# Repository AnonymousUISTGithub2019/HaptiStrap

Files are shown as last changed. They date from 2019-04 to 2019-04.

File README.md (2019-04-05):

# What is the HaptiStrap?


How tightly a haptic device, such as a smartwatch, is strapped to the body can change how its vibrotactile effects are perceived.
Although a single researcher may be able to achieve reasonably consistent strap tightness across participants, this may not be easily achievable when multiple, potentially geographically distributed, experimenters are working with different participants.
Likewise, when participants must attach the devices on their own, e.g., during a longitudinal in-the-wild study, they may not use the same tightness each day.

The HaptiStrap is a low-cost, easily fabricated tool, loosely based on the medical Gulick tape measure, that helps to create consistent strap tension, and therefore haptic coupling, for wearable haptic devices used in user studies.
Since it is fabricated using 3d printing, the HaptiStrap can be easily modified to meet the requirements for a variety of body locations and experiment types.
Although HaptiStrap is not yet trialed with users, we present design iterations motivated by problems seen in our own work, as a contribution towards designing a standard method for ensuring that studies do better than vague ``tight but comfortable'' guidelines.

In this repository you will find all necessary files, fabrication, assembly and usage instructions to integrate the HaptiStrap in your project. In addition, since OpenSCAD design files are provided, a short step-by-step example is provided to adapt the HaptiStrap device to a different strap width. 

If you use the HaptiStrap, please do not forget to cite this publication:

INSERT PAPER BILIOGRAPHY ENTRY HERE.

# Table of Content
- [Making your Own HaptiStrap](#making-your-own-haptistrap)
  * [Equipment](#equipment)
  * [Choosing a Tensioner](#choosing-a-tensioner)
  * [3D Printing](#3d-printing)
    + [Get the Files](#get-the-files)
    + [Print the Files](#print-the-files)
  * [Putting it all Together](#putting-it-all-together)
    + [Elastic Tensioner](#elastic-tensioner)
    + [3D Printed Tensioner](#3d-printed-tensioner)
- [Using the HaptiStrap in your Project](#using-the-haptistrap-in-your-project)
  * [Determining how Many Elastics to use](#determining-how-many-elastics-to-use)
  * [Customizing HaptiStrap Dimensions to Match your Project](#customizing-haptistrap-dimensions-to-match-your-project)
  * [Adding the HaptiStrap to your Haptic System](#adding-the-haptistrap-to-your-haptic-system)
  * [Recommended Placement Instructions](#recommended-placement-instructions)
 
# Making your Own Haptistrap 

## Equipment
You will need access to the following equipment to make and assemble your own HaptiStrap:

1. FDM 3D printer
2. PLA filament (approximately 5 g or 2 m)
3. Orthodontic elastics (1/8", 1.8oz)
4. Pointy tweezers (useful for placing the elastics)
5. Highly visible permanent coating material (e.g., white/neon paint/nail polish, liquid paper, etc.)
6. Low-friction tape (e.g., teflon, aluminium, polyethylene tape etc.)

## Choosing a Tensioner

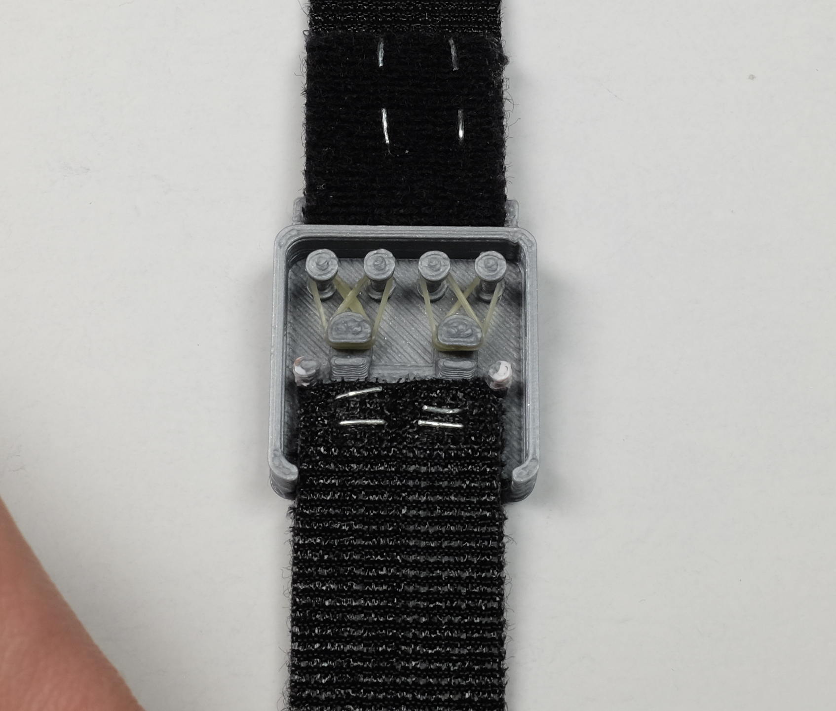
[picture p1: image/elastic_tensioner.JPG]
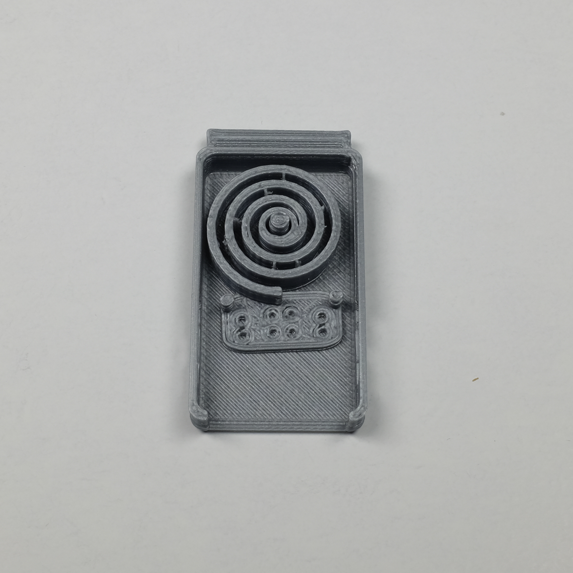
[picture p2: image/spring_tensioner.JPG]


Despite making the 3D printed spring option available, we highly recommend using the elastic tensioner system as it was shown to have more consistent mechanical properties.

## 3D Printing 

### Get the Files

Before printing your own HaptiStrap, you will need to download the pre-rendered STL files or generate them from the provided OpenSCAD design files.

The type of tensioner you want to use dictates the path and file name of the files to download.

| Tensioner Type | File|
|---|---|
|elastic|/stl/elastic/haptistrap_enclosure_elastic.stl|
||/stl/elastic/haptistrap_tensioner_elastic.stl|
||/stl/elastic/haptistrap_elastic_primer.stl|
|3D printed spring|/stl/3dPrintedSpring/haptistrap_enclosure_spring.stl|
||/stl/3dPrintedSpring/haptistrap_tensioner_spring.stl|
||/stl/3dPrintedSpring/haptistrap_spring_primer.stl|

### Print the Files

The HaptiStrap was designed such that it can be printed with the most commonly encountered 3D printer configuration, material (PLA) and slicing settings.

The following slicing parameters were used to obtain the components whose properties were measured and reported in the HaptiStrap paper. While you are free to modify any of them, these modifications could influence the mechanical properties of the produced component. 

| Parameter | Value | Unit |
|---|---|---|
|nozzle size|0.4|mm|
|layer height|0.2|mm|
|line width|0.4|mm|
|wall thickness|0.8|mm|
|top/bottom thickness|0.8|mm|
|infill density|100|%|

Notes:
- Supports should be used to ensure that the calibration windows on each side of the enclosure and lid are properly aligned.
- A brim, skirt or raft can be used to print the enclosure and its lid depending on your bed adhesion.
- For the 3D printed spring tensioner, it is preferable to print on a very smooth surface (e.g., glass, mirror, etc.) as the texture may increase friction between the spring and enclosure. As such, the use of a raft or brim is not recommended.

## Putting it all Together

Separate assembly instructions are provided depending on the type of tensioner used.

### Elastic Tensioner

|Instruction|Picture|
|---|-----|
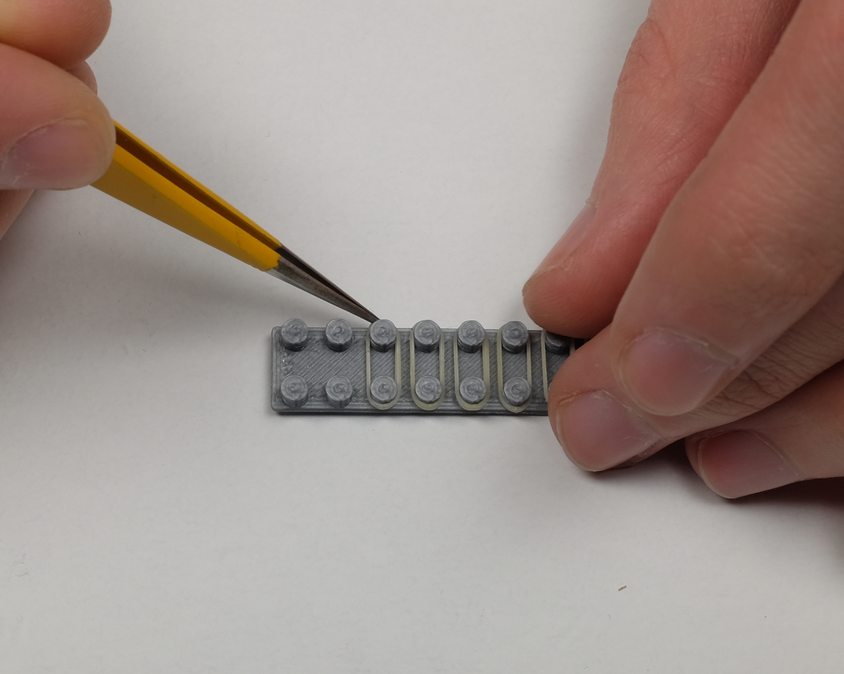
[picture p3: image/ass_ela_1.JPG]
|1. Place each elastic on the 3d printed elastic primer and wait for at least six (6) hours for their properties to settle.||
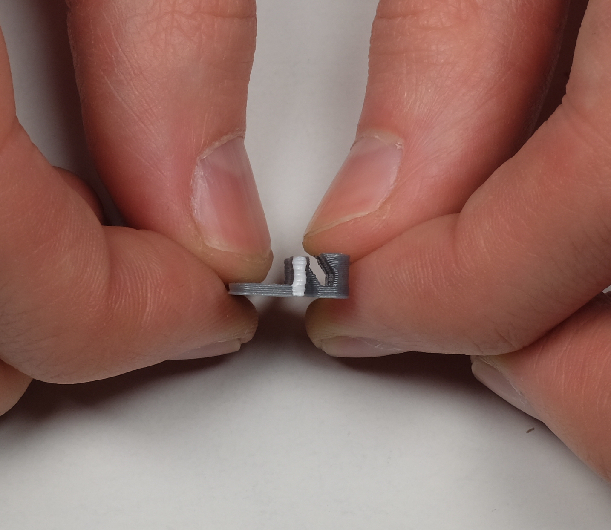
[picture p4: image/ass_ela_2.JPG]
|2. Coat the pin on each side of the tensioner with highly visible material||
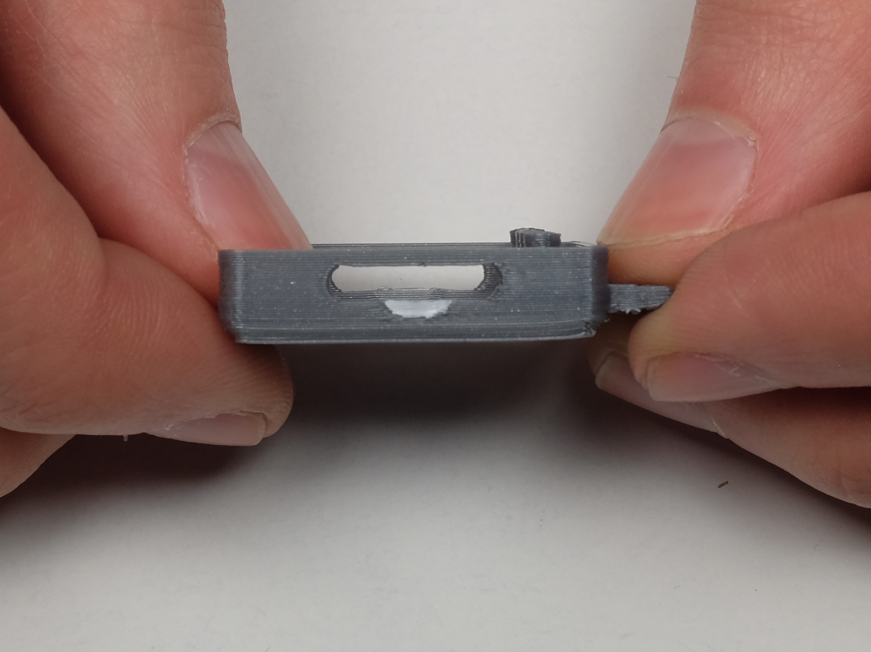
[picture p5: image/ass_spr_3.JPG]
|3. Coat the indented half-circle on each side of the enclosure with highly visible material||
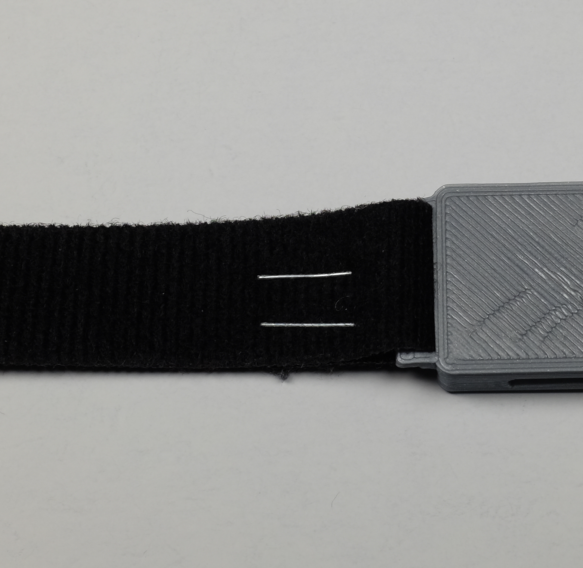
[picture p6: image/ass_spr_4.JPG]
|4. Sew or staple a piece of velcro to the enclosure||
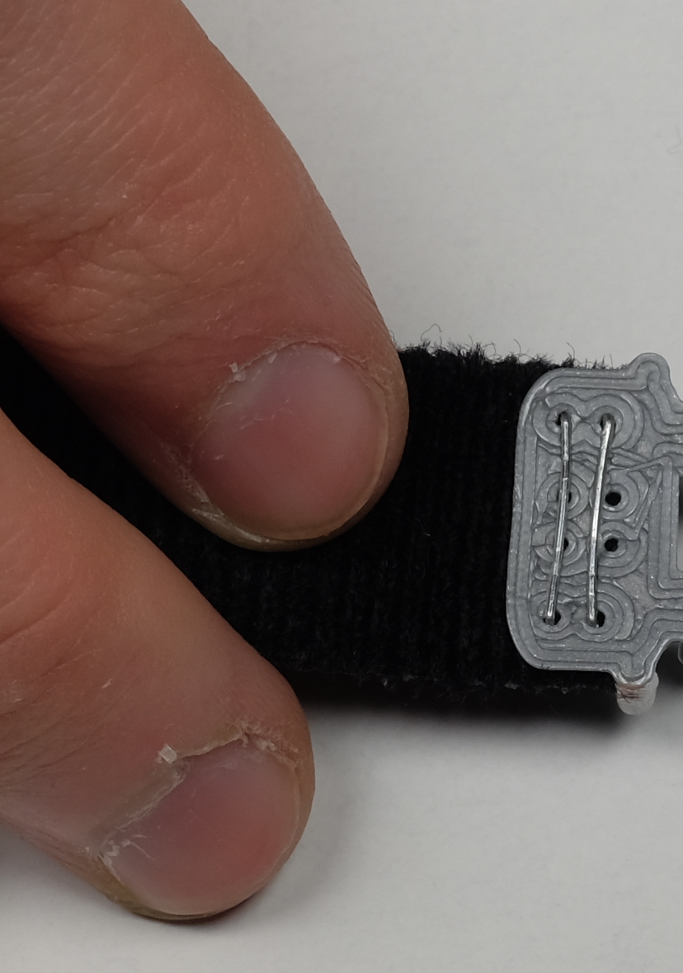
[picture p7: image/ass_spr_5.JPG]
|5. Sew or staple a second piece of velcro to the tensioner||
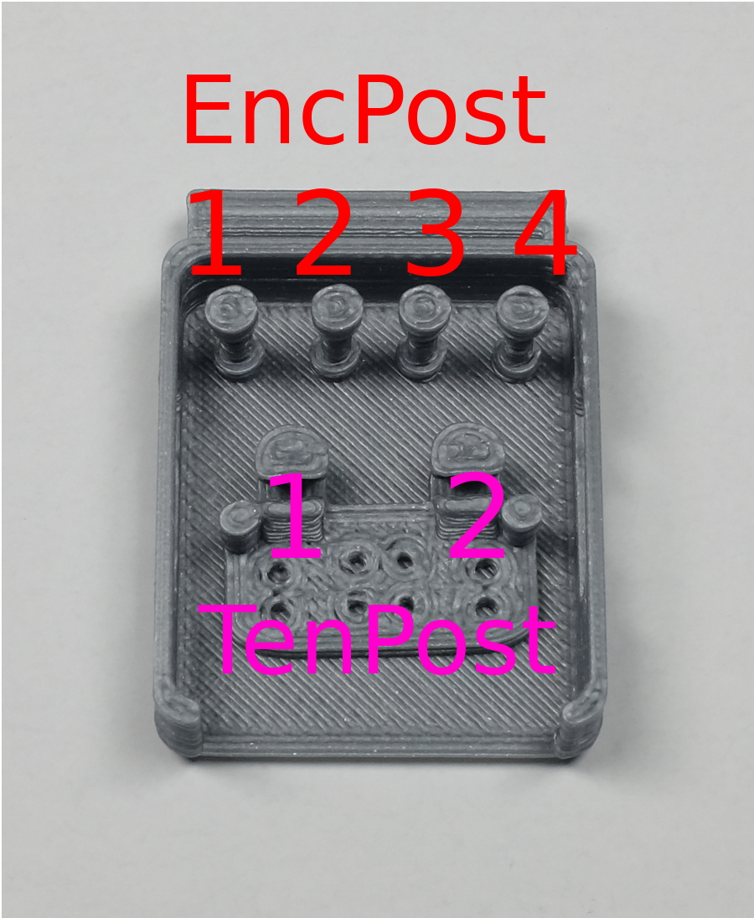
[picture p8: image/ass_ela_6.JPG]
|6. Using the pointy tweezers, carefully place the elastics such that forces are balanced between posts and that the elastics do not overlap. E.g.: EncPost1-TenPost1, EncPost4-TenPost2, EncPost2-TenPost1, EncPost3-TenPost2||
|7. Put the lid on||

To reduce friction and the likelihood of introducing vibration artifacts, we recommend applying a piece of low-friction tape (e.g., aluminium tape, polyethylene Film Tape, etc.) to the portion of the strap that is inside the enclosure at rest and the inside of the enclosure.

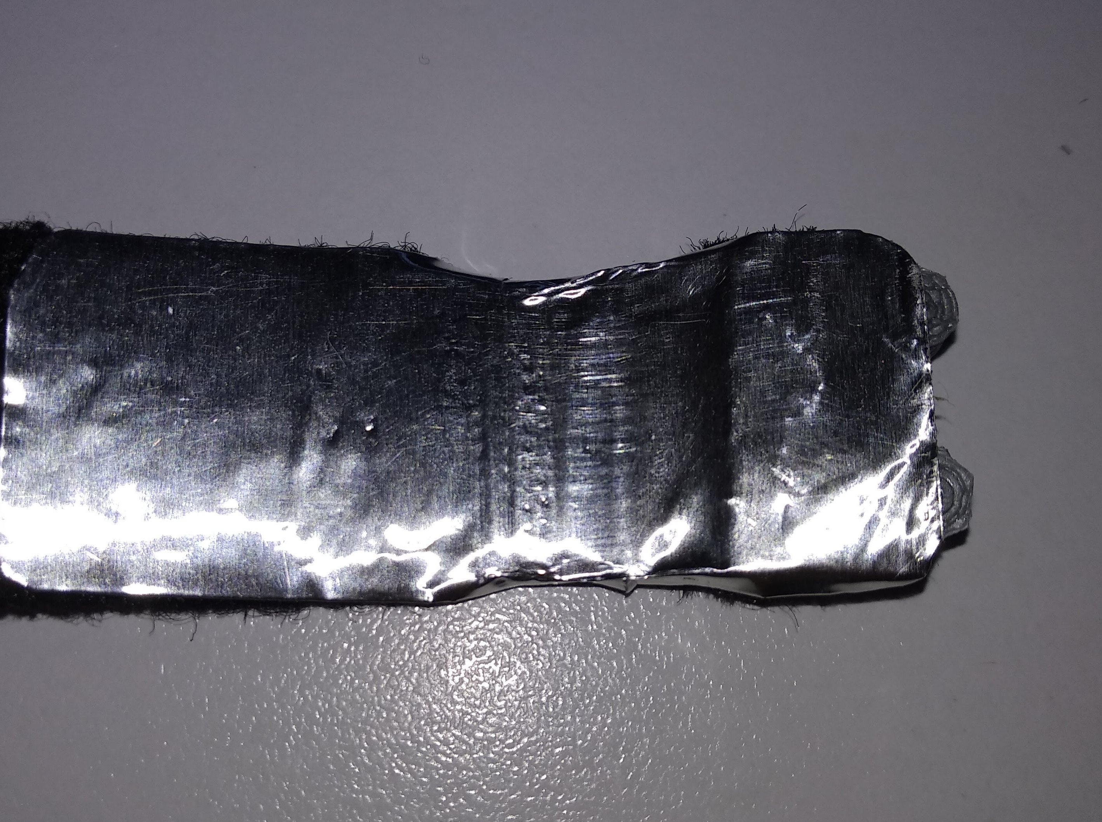
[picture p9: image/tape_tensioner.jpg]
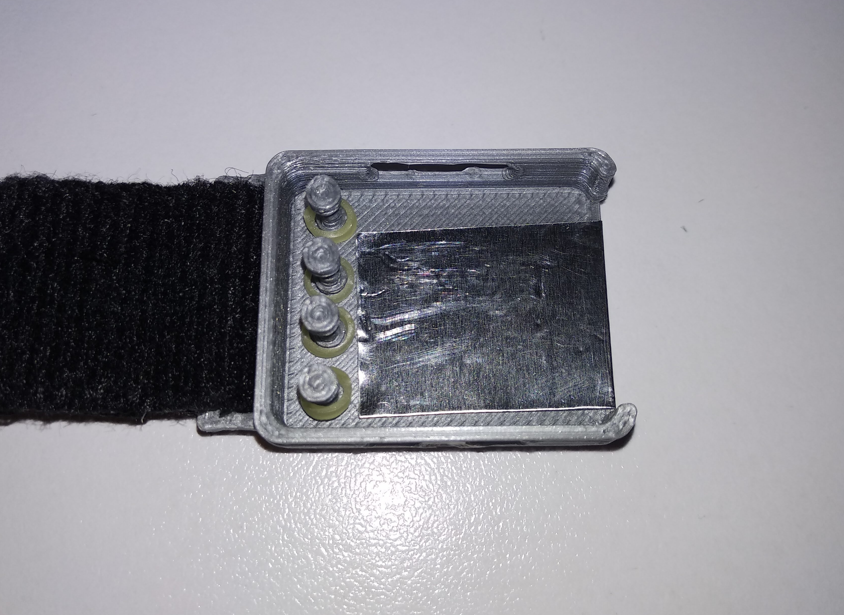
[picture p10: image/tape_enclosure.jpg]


### 3D Printed Tensioner

|Instruction|Picture|
|---|---|
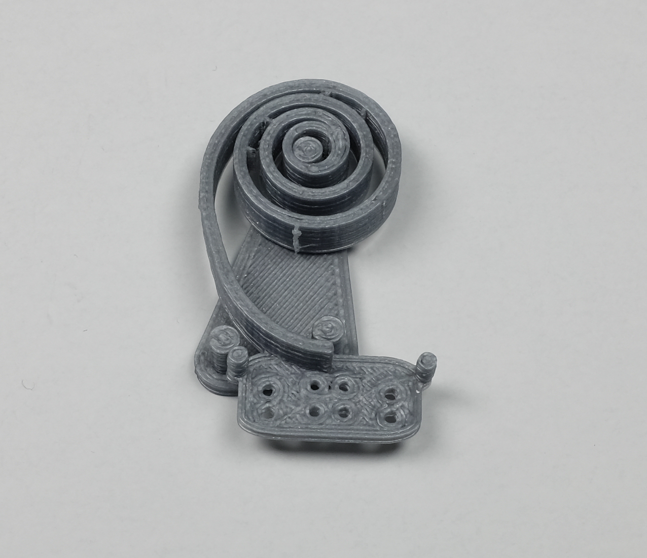
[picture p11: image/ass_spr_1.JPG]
|1. Place the 3d printed spring on the primer and wait for at least six (6) hours for its properties to settle.||
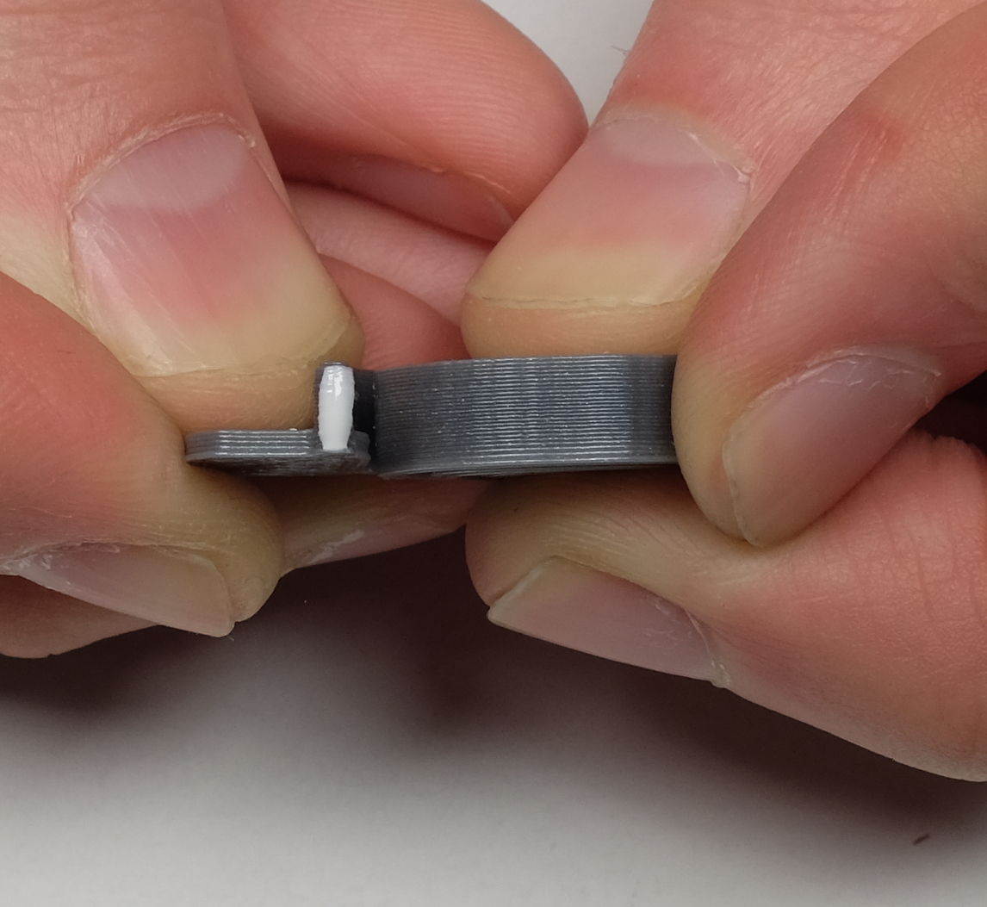
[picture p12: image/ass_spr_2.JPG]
|2. Coat the pin on each side of the tensioner with highly visible material||
|3. Coat the indented half-circle on each side of the enclosure with highly visible material||
|4. Sew or staple a piece of velcro to the enclosure||
|5. Sew or staple a second piece of velcro to the tensioner||
|6. Insert the tensioner in the enclosure by inserting the post in the opening in the center of the spring||
|7. Put the lid on||

# Using the HaptiStrap in your Project

## Determining how Many Elastics to Use 

The number of orthodontic elastics used in the HaptiStrap will directly modify the tension exerted by the tensioner on the overall system.

A calculator is provided to assist you in estimating the number of elastics needed for your specific application.

Calculator:
https://docs.google.com/spreadsheets/d/1YI04TUiVzIxZJ8hUbnIkhWvlUe_tBS4BZTtzd4iJfN4/edit?usp=sharing

## Customizing HaptiStrap Dimensions to Match your Project

The OpenSCAD design files available in the path /CAD/src/ allow you to customize the HaptiStrap to the specifications of your haptic project.

Here is an example, outlining the steps required to modify the enclosure dimension to accomodate for a 25 mm wide strap instead of the current 20 mm.

1. In file "haptistrap_enclosure.scad", change the value of strap_w, on line 46, from 20 to 25. By refreshing the preview, you will notice that this has widened the hole through which the strap enters the enclosure, and also the buckle through which the enclosure is attached to the strap.
2. In file "haptistrap_enclosure.scad", change the enclosure width by changing the value of o_w, on line 31, from 25 mm to 30 mm.
3. In file "haptistrap_tensioner.scad", change the tensioner's width by changing the value of o_w, on line 33, from 25 mm to 30 mm. This will reposition the elastic slots and bring the calibration pins closer to the outside walls. Note that it does not widen the base plate.
4. Render the model for each .scad file by using F6, or the button at the top of OpenSCAD's window.
5. Generate STL files for each .scad file by pressing the "stl" button at the top of OpenSCAD's window.

## Adding it to your Haptic System

The HaptiStrap must be inserted in series with your system's inelastic strap and haptic rendering component such that all of the tension goes through the tensioner.

Here is an example of how the HaptiStrap can be used with an original Pebble smartwatch:



## Recommended Placement Instructions

Here is a set of recommended placement instructions that allows to position both the HaptiStrap and haptic rendering system in a precise location when using a velcro strap:
1. Position and hold the Haptistrap in a comfortable position on the desired limb.
2. Position and hold the haptic rendering system where desired.
3. Pull on the velcro strap away from the limb, such that the visual indicators on both the tensioner and the enclosure are aligned.
4. Maintaining the tension, wrap the velcro strap around the limb such that it is secured to the rest of the system.
5. Validate that the visual indicators are still aligned, readjust as needed.

# Credit 
This work makes use of the "Achimedean Spiral Module" (CC BY 3.0: https://creativecommons.org/licenses/by/3.0/) by user "Manticorp", available on thingiverse: https://www.thingiverse.com/thing:1267784

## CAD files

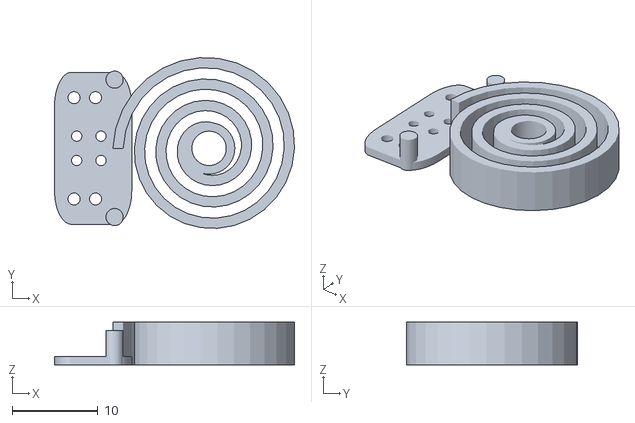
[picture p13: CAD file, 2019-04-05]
CAD/stl/3dPrintedSpring/haptistrap_link_spring.stl
27.9 x 19.9 x 5.00

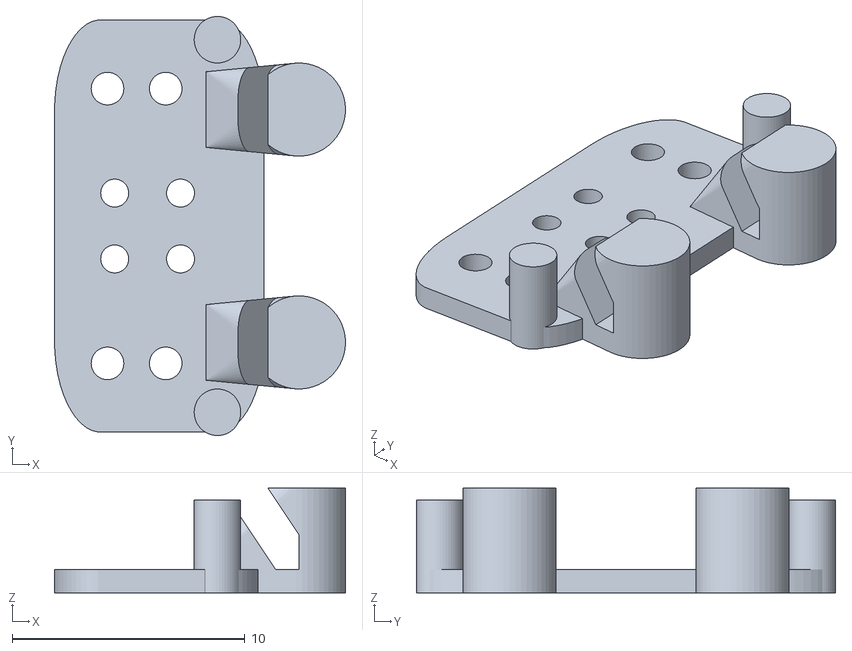
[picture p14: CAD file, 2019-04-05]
CAD/stl/elastic/haptistrap_link_elastic.stl
12.5 x 18.0 x 4.50

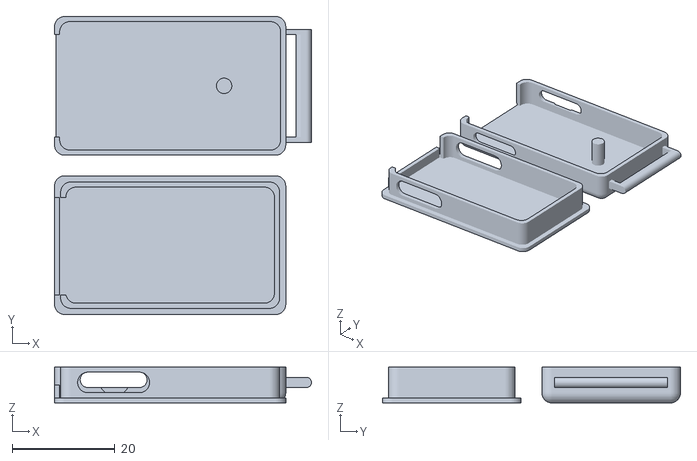
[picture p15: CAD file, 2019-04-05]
CAD/stl/3dPrintedSpring/haptistrap_enclosure_spring.stl
50.0 x 58.0 x 7.00

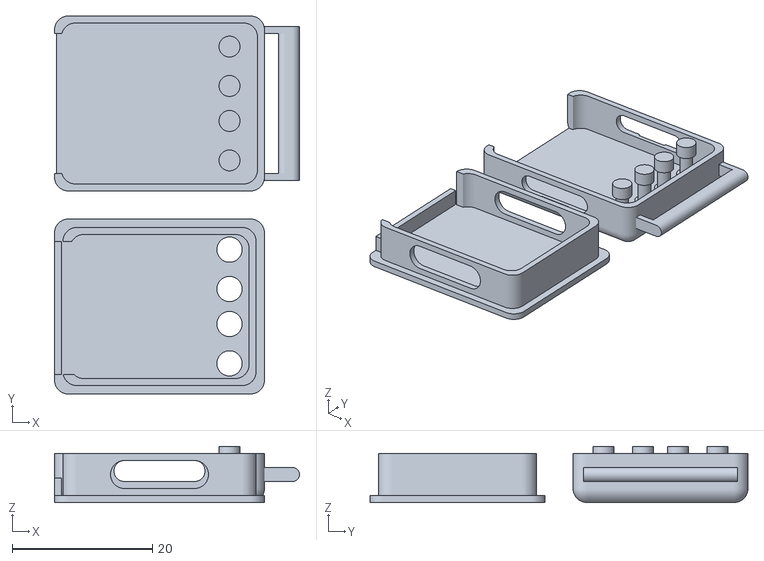
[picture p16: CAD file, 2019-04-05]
CAD/stl/elastic/haptistrap_enclosure_elastic.stl
35.0 x 54.0 x 8.00

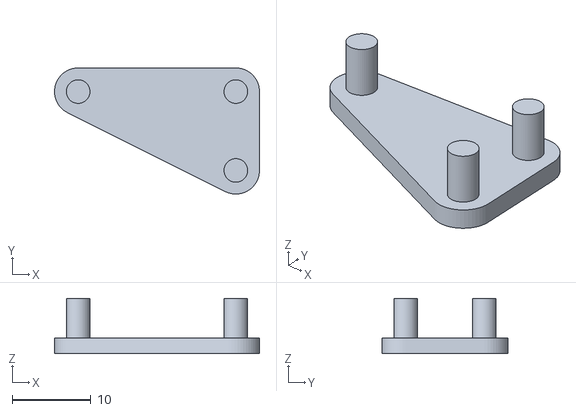
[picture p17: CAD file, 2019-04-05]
CAD/stl/3dPrintedSpring/haptistrap_spring_primer.stl
26.0 x 16.0 x 7.00

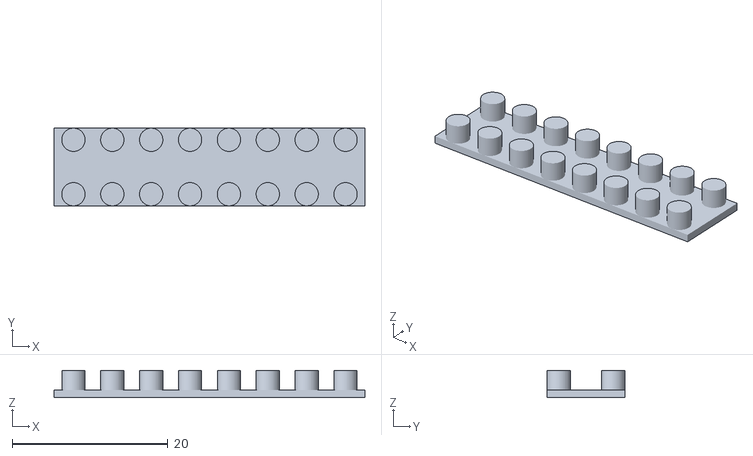
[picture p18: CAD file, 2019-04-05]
CAD/stl/elastic/haptistrap_elastic_primer.stl
40.0 x 10.0 x 3.50

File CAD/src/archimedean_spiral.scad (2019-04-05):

// spirals   = how many spirals
// thickness = how thick you want the arms to be
// rmax      = maximum radius
linear_extrude(5)
    archimedean_spiral(1,0.8,10);

module archimedean_spiral(spirals=1, thickness=1, rmax = 100){
    s = spirals*360;
    t = thickness;
    a = sqrt(pow(rmax,2)/(pow(s,2)*(pow(cos(s),2) + pow(sin(s),2))));
    points=[
        for(i = [0:$fa:s]) [
            (i*a)*cos(i),
            (i*a)*sin(i)
        ]
    ];
    points_inner=[
        for(i = [s:-$fa:0]) [
            (((i*a)+t)*cos(i)),
            (((i*a)+t)*sin(i))
        ]
    ];
    polygon(concat(points,points_inner));
}

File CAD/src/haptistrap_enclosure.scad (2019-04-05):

//Title: haptistrap_enclosure
//Project: HaptiStrap
//Author: BLINDED
//Affiliation: BLINDED
//
//Description: Design file for HaptiStrap enclosure. Can generate an enclosure for both the elastic and printed tensioner designs. To adapt to tensioner type, modify lines 18-19 and 26-27. Lines 14-15 can also be used to control whether the enclosure and/or lid should appear on the generated model.

// For optimization, limit circles to 50 facets 
$fn=50;

// Whether the enclosure and lid should be included in the file (for generating STL/printing)
// Set to 1 if you want enclosure/lid
wENCLOSURE = 1;
wLID = 1;

// SET TO 1 TO SELECT TENSIONER TYPE
use_printed_tensioner = 0;
use_elastic_tensioner = 1;

//********************     DIMENSIONS     *******************
// ENCLOSURE MEASUREMENTS
// outside measurements (Excludes lid dimensions)

// ** UNCOMMENT LINE DEPENDING ON TENSIONER TYPE **
// Length
//o_l = 45; // Uncomment for printed tensioner
o_l = 30; // Uncomment for elastic tensioner

// Width
//o_w = 27; // Uncomment for printed tensioner
o_w = 25; // Uncomment for elsatic tensioner

// Thickness
o_th = 7;

// Wall Thickness
wall_th = 1;

// Bottom and top thickness
bottop_th = 1;

// Corner smooth radius
smooth_rad = 2;

// Strap width
strap_w = 20;

// Calibration Window Dimensions
cal_l = 10;
cal_w = 3;

// Parameters for elastic model
// Shaft that hold the elastic on the mobile part
shaft_r = 1.5;

// Distance between the two pegs to hold the elastic
dist_post = 2*shaft_r+0.75;

// Distance between the pegs and the front wall (larger = closer to back wall)
peg_back_dist = 5*o_l/6;

// Parameters for printed spring model
dist_post_back = 12;

// 3d printed spring priming offset
priming_offset = 3;

// *************** GENERATE ENCLOSURE ******************
enclosure(); // Insert a generic lid and enclosure with a T_spring_connector
main_buckle(); // Translate upwards to compensate for rounded bottom

module enclosure(){

if (wENCLOSURE ==1){
    difference(){
        difference(){
            difference(){ // Diff between outter case shell and inner case shell
                hull(){ // Outter shell of the case
                    translate([smooth_rad, smooth_rad, smooth_rad]){
                        cylinder(r=smooth_rad, h=o_th-smooth_rad);
                        sphere(r=smooth_rad);
                    }
                    translate([o_l-smooth_rad, smooth_rad, smooth_rad]){
                        cylinder(r=smooth_rad, h=o_th-smooth_rad);
                        sphere(r=smooth_rad);
                    }
                    translate([o_l-smooth_rad, o_w-smooth_rad, smooth_rad]){
                        cylinder(r=smooth_rad, h=o_th-smooth_rad);
                        sphere(r=smooth_rad);
                    }
                    translate([smooth_rad, o_w-smooth_rad, smooth_rad]){
                      cylinder(r=smooth_rad, h=o_th-smooth_rad);
                      sphere(r=smooth_rad);  
                    } 
                }
                hull(){ // Inner shell of the case
                    translate([smooth_rad+wall_th, smooth_rad+wall_th, bottop_th])
                        cylinder(r=smooth_rad, h=o_th-bottop_th);
                                
                    translate([o_l-smooth_rad-wall_th, smooth_rad+wall_th, bottop_th])
                        cylinder(r=smooth_rad, h=o_th-bottop_th);
                                
                    translate([o_l-smooth_rad-wall_th, o_w-smooth_rad-wall_th, bottop_th])
                        cylinder(r=smooth_rad, h=o_th-bottop_th);
                                
                    translate([smooth_rad+wall_th, o_w-smooth_rad-wall_th, bottop_th])
                        cylinder(r=smooth_rad, h=o_th-bottop_th);   
                }
            }

            // Strap opening in enclosure
            translate([-1.5/wall_th,o_w/2-strap_w/2,bottop_th])
                cube([4*wall_th, strap_w, o_th]);
        }    
      
         if (use_printed_tensioner==1){
            translate([o_l-dist_post_back*2-cal_w/2-priming_offset, 0, 3*cal_w/2])
                        rotate([90,0,0])
                        hull(){
                            translate([-cal_l,0,0])
                                cylinder(r=cal_w/2, h=300, center=true);
                                cylinder(r=cal_w/2, h=300, center=true);
                        }
                
            // Make center window on "right" side of enclosure
            translate([o_l-dist_post_back*2-cal_w/2-(cal_l)/3- (cal_w*1.01)/2-priming_offset, wall_th/3, 3*cal_w/2])    
                difference(){
                hull(){
                    translate([0,0,0])
                        rotate([90,0,0]) cylinder(r=cal_w*1.01, h=wall_th/3);
                    translate([0,0,0])
                        rotate([90,0,0]) cylinder(r=cal_w*1.01, h=wall_th/3);
                }
                translate([0,0,2.5]) cube([10,5,5], center=true);
            }
            
            // Make center window on "left" side of enclosure
            translate([o_l-dist_post_back*2-cal_w/2-(cal_l)/3- (cal_w*1.01)/2-priming_offset, o_w, 3*cal_w/2])    
                difference(){
                hull(){
                    translate([0,0,0])
                        rotate([90,0,0]) cylinder(r=cal_w*1.01, h=wall_th/3);
                    translate([0,0,0])
                        rotate([90,0,0]) cylinder(r=cal_w*1.01, h=wall_th/3);
                }
                translate([0,0,2.5]) cube([10,5,5], center=true);
            }
        }
        
        if (use_printed_tensioner==0){
                translate([o_l-peg_back_dist+5, 0, 3*cal_w/2]) 
                     rotate([90,0,0])
                        hull(){
                            translate([cal_l,0,0])
                                cylinder(r=cal_w/2, h=300, center=true);
                            translate([0,0,0])
                                cylinder(r=cal_w/2, h=300, center=true);
                        }
                            
                 // Make center window on "right" side of enclosure
                translate([o_l-peg_back_dist+5+(cal_l)/3+(cal_w*1.01)/2, wall_th/3, 3*cal_w/2]) 
                    difference(){
                    hull(){
                        translate([0,0,0])
                            rotate([90,0,0]) cylinder(r=cal_w*1.01, h=wall_th/3);
                        translate([0,0,0])
                            rotate([90,0,0]) cylinder(r=cal_w*1.01, h=wall_th/3);
                    }
                    translate([0,0,2.5]) cube([10,5,5], center=true);
                }
                
                // Make center window on "left" side of enclosure
                translate([o_l-peg_back_dist+5+(cal_l)/3+(cal_w*1.01)/2, o_w, 3*cal_w/2]) 

                    difference(){
                    hull(){
                        translate([0,0,0])
                            rotate([90,0,0]) cylinder(r=cal_w*1.01, h=wall_th/3);
                        translate([0,0,0])
                            rotate([90,0,0]) cylinder(r=cal_w*1.01, h=wall_th/3);
                    }
                    translate([0,0,2.5]) cube([10,5,5], center=true);
                }
                                
        }  
    }
    
    // Post for spirale spring
    if (use_printed_tensioner==1){
        translate([o_l-dist_post_back, o_w/2, bottop_th])
            cylinder(r=1.5, h=o_th-bottop_th);
    }
    
    
    // Posts for elastics
    if (use_elastic_tensioner==1){
    shaft_r = 1.5;
    dist_post = 2*shaft_r+0.75;
        
    translate([peg_back_dist, o_w/4+dist_post, bottop_th])
        elastic_post();
         
    translate([peg_back_dist, 3*o_w/4+dist_post/1/2, bottop_th])
        elastic_post();
        
    translate([peg_back_dist, o_w/4-dist_post/1/2, bottop_th])
        elastic_post();

        
    translate([peg_back_dist, 3*o_w/4-dist_post, bottop_th])
        elastic_post();
        
    }

}
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

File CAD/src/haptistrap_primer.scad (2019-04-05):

//Title: haptistrap_elastic_primer
//Project: HaptiStrap
//Author: BLINDED
//Affiliation: BLINDED
//
//Description: Design file for the elastic primer. Change line 13 to the number of elastics that should be pre-stretched.


// Number of faces on cylinders, sphere, etc.
$fn=50;

use_printed_tensioner = 1;
use_elastic_tensioner = 0;

// Number of elastics to prime
n_elastics = 8;

if (use_elastic_tensioner == 1){
    // Base plate
    translate([n_elastics*5/2,0,1]) cube([n_elastics*5, 10, 1], center=true);

    // Place posts on base plate
    for (n=[1:n_elastics]){
        translate([(n-1)*5+2.5,0,0]){
            translate([0,-5+1.5,1]) cylinder(r=1.5, h=3);
            translate([0,5-1.5,1]) cylinder(r=1.5, h=3);
        }
    }
}

if (use_printed_tensioner == 1){
    // base plate
    hull(){
        cylinder(r=3, h=2);
        translate([20,0,0]) cylinder(r=3, h=2);
        translate([20,-10,0]) cylinder(r=3, h=2);
    }
    
    // posts
    cylinder(r=1.5, h=7);
    translate([20,0,0]) cylinder(r=1.5, h=7);
    translate([20,-10,0]) cylinder(r=1.5, h=7);

}

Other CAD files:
CAD/src/haptistrap_tensioner.scad
